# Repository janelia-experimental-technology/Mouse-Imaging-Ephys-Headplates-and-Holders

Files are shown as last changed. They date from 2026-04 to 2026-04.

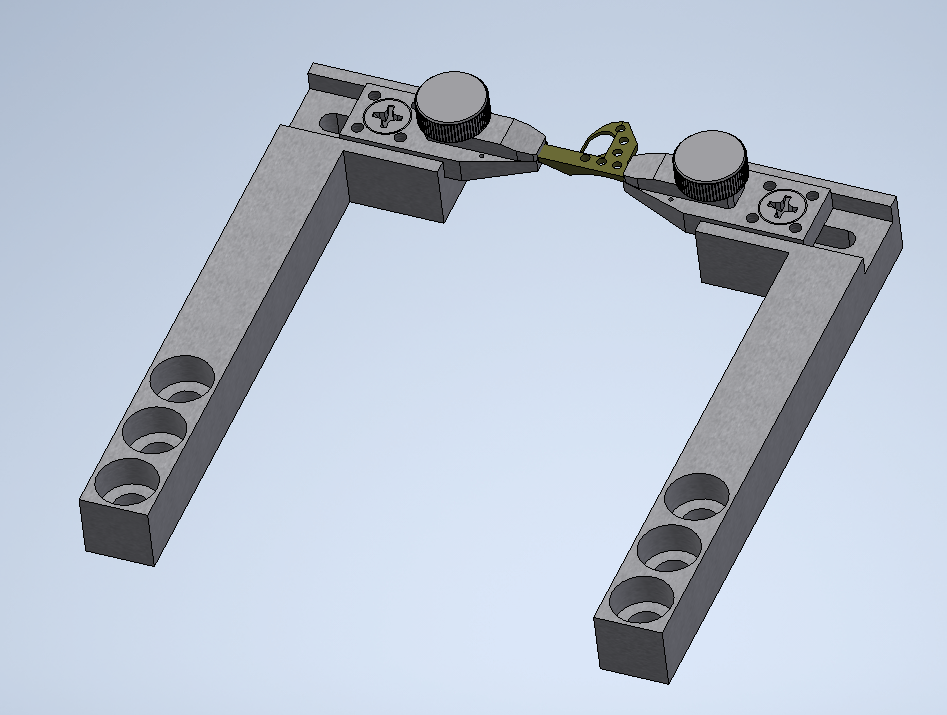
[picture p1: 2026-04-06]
Headbar and Holders.png

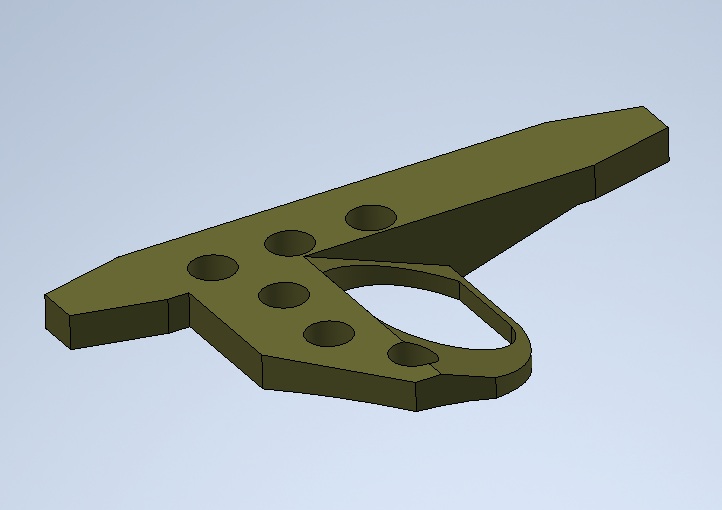
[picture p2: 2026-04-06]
Barrel Sloped Headbar.png

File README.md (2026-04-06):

### Mouse Headplates and Holders for Imaging and Electrophysiology

Researchers at Janelia have designed several head plates for live mouse imaging and electrophysiology experiments in collaboration with jET. 

The head plates are attached to the skull of the mouse typically with dental cement, and are used to locate the brain to the microscope. 

The Barrel Ctx Plate (Sloped Left) Headpost was developed by and used extensively in the Svoboda lab for in vivo imaging of the barrel cortex and other cortical areas (e.g. Huber et al 2012). The Headpost with three epoxy holes was used by the Svoboda lab for electrophysiology experiments. 

Opportunity: Free to make for Non-Profit Research by downloading the design here. See included hardware license.

Rights and designs available for Commercial License. Janelia makes no endorsements or guarantees of licensee products.

For inquiries, please contact innovation@janelia.hhmi.org and reference this repository.

To cite the designs, please use DOI: https://doi.org/10.25378/janelia.31945893

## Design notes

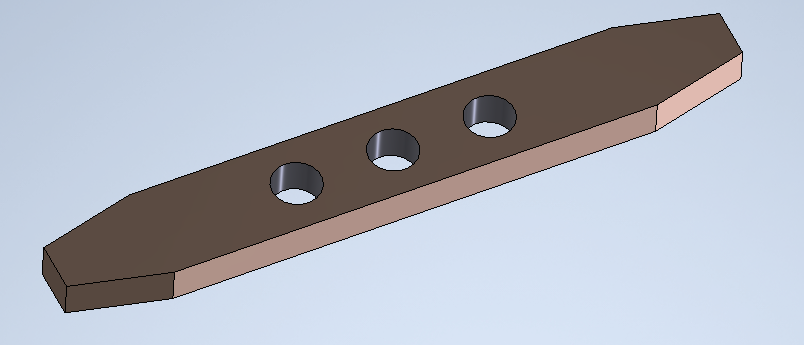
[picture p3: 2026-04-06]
3 Hole Headbar.png

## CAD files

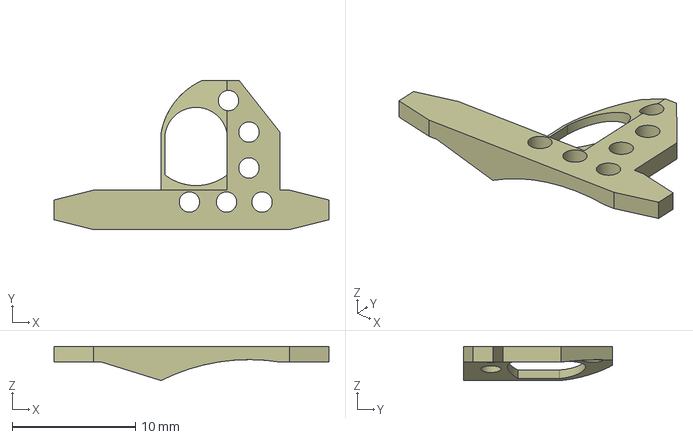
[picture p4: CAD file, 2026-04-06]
Part Files/JF-JM-HC0011 BarrelCtxPlateSlopedLeft Rev A.stp
22.3 x 12.1 x 2.77 mm

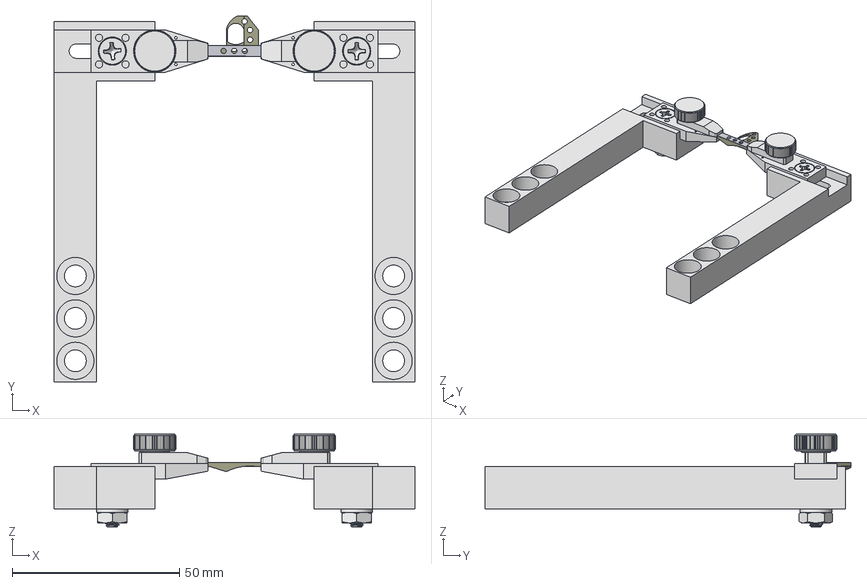
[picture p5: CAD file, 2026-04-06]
Assembly Files/J005779 HEAD POST AND MOUNTING BARS Rev A.stp
107.9 x 109.6 x 27.8 mm
JF-JM-HC0011
J005774 x 2
J005776 x 2
J005772
J005771
91771A197 x 2
92141A009 x 2
91185A440 x 2
91841A009 x 2
J001375

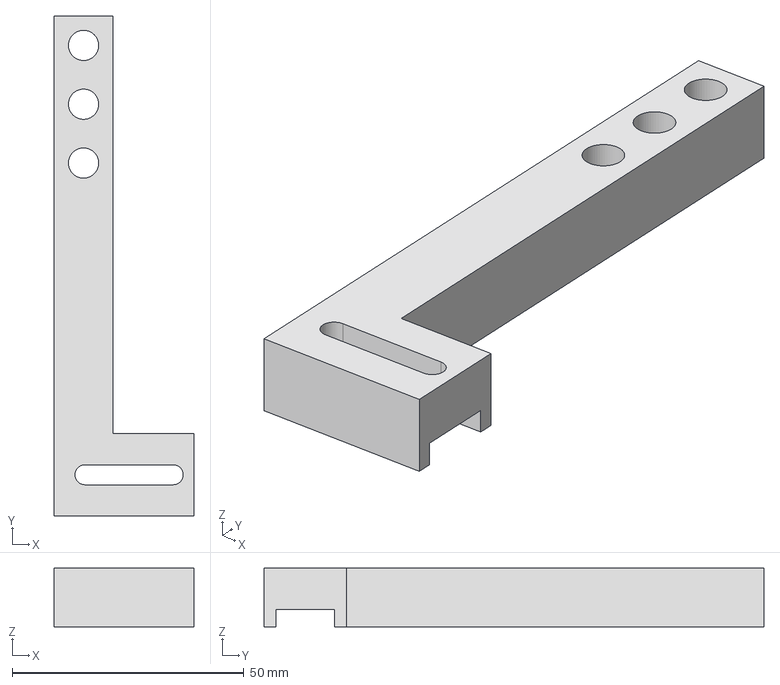
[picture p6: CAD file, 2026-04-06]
Part Files/J005772 HEAD MOUNT ARM ML Rev -.stp
30.1 x 107.9 x 12.7 mm

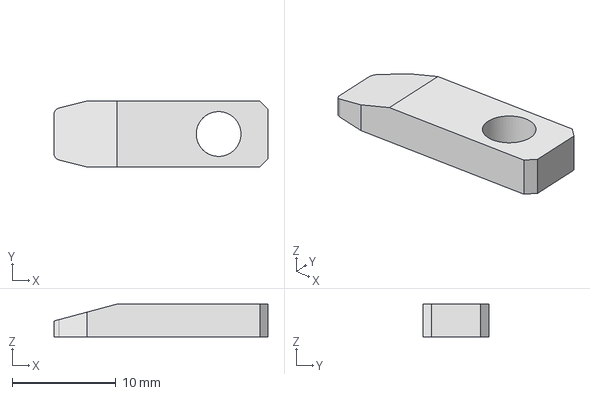
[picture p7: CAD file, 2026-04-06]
Part Files/J005776 HeadPostHolderTop Rev -.stp
20.6 x 6.35 x 3.17 mm

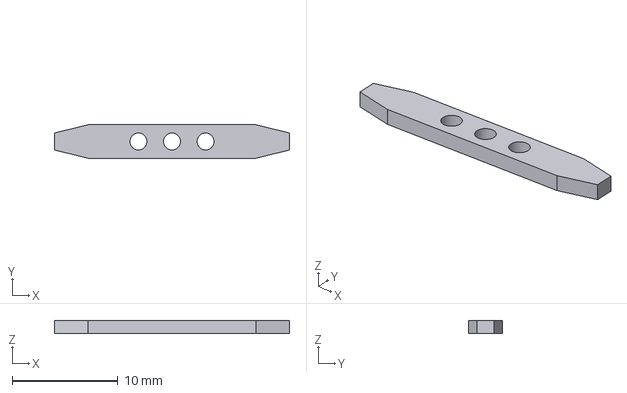
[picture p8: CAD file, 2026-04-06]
Part Files/J001375 KS style headpost with three epoxy holes Rev -.stp
22.2 x 3.18 x 1.27 mm

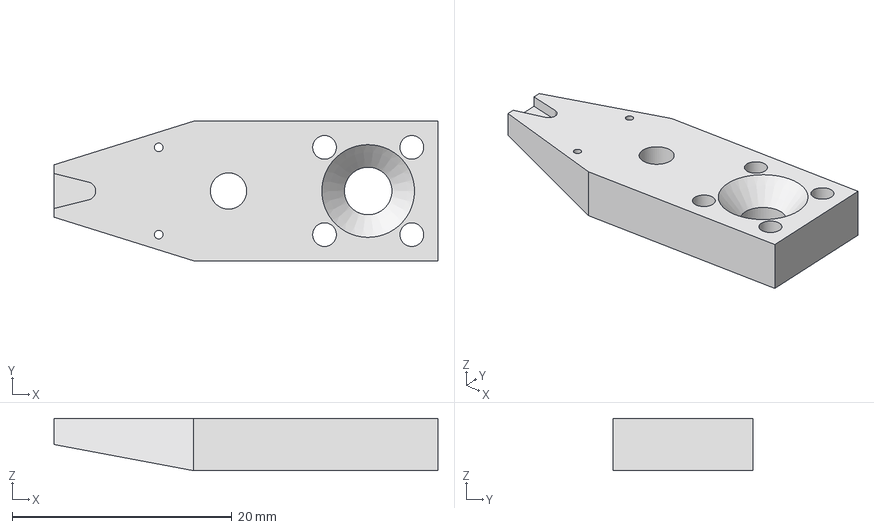
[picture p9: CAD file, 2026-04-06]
Part Files/J005774 HeadPostHolderBottom Rev -.stp
34.9 x 12.7 x 4.76 mm

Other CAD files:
Part Files/J005771 HEAD MOUNT ARM MR Rev -.stp
Inventor Pack And Go/91185A440.ipt
Inventor Pack And Go/91771A197.ipt
Inventor Pack And Go/91841A009.ipt
Inventor Pack And Go/92141A009.ipt
Inventor Pack And Go/BarrelCtxPlateSlopedLeft.ipt
Inventor Pack And Go/HEAD MOUNT ARM ML.ipt
Inventor Pack And Go/HEAD MOUNT ARM MR.ipt
Inventor Pack And Go/HEAD POST AND MOUNTING BARS.iam
Inventor Pack And Go/HeadPostHolderBottom.ipt
Inventor Pack And Go/HeadPostHolderTop.ipt
Inventor Pack And Go/KS style headpost with three epoxy holes.ipt

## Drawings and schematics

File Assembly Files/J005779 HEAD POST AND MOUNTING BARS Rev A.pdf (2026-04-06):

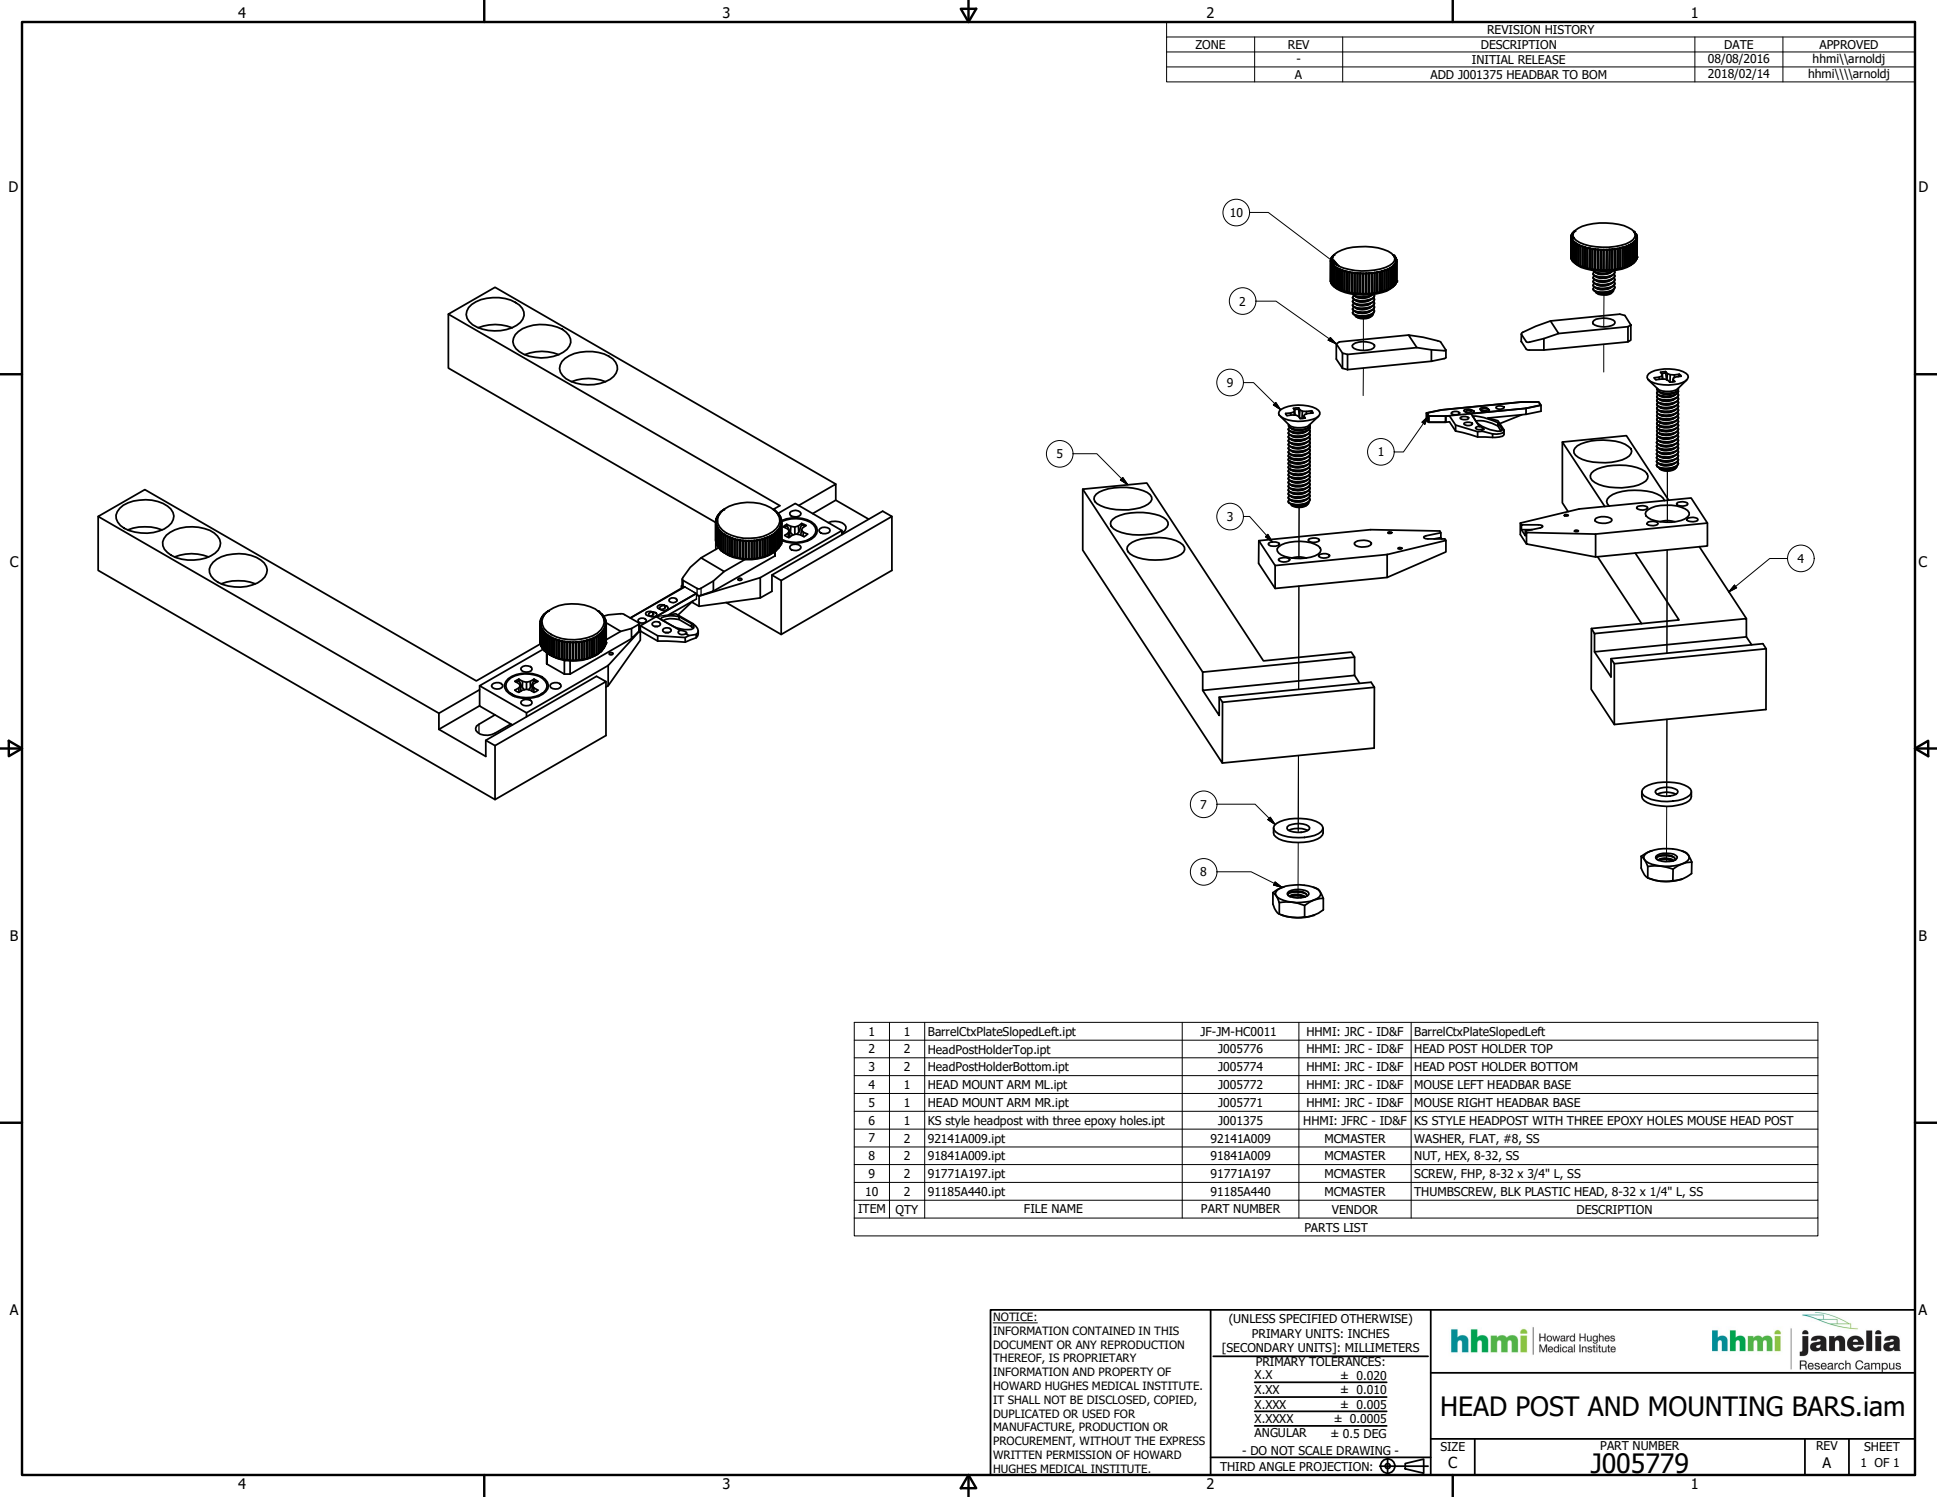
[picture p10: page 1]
PARTS LIST; PART NUMBER; 1 OF 1 THIRD ANGLE PROJECTION:; ± 0.020 ± 0.010 ± 0.005 ± 0.0005 ± 0.5 DEG; REVISION HISTORY

ZONE | REV | DESCRIPTION | DATE | APPROVED

- | INITIAL RELEASE | 08/08/2016 | hhmi\\arnoldj
A | ADD J001375 HEADBAR TO BOM | 2018/02/14 | hhmi\\\\arnoldj

1 | 1 | BarrelCtxPlateSlopedLeft.ipt | JF-JM-HC0011 | HHMI: JRC - ID&F | BarrelCtxPlateSlopedLeft
2 | 2 | HeadPostHolderTop.ipt | J005776 | HHMI: JRC - ID&F | HEAD POST HOLDER TOP
3 | 2 | HeadPostHolderBottom.ipt | J005774 | HHMI: JRC - ID&F | HEAD POST HOLDER BOTTOM
4 | 1 | HEAD MOUNT ARM ML.ipt | J005772 | HHMI: JRC - ID&F | MOUSE LEFT HEADBAR BASE
5 | 1 | HEAD MOUNT ARM MR.ipt | J005771 | HHMI: JRC - ID&F | MOUSE RIGHT HEADBAR BASE
6 | 1 | KS style headpost with three epoxy holes.ipt | J001375 | HHMI: JFRC - ID&F | KS STYLE HEADPOST WITH THREE EPOXY HOLES MOUSE HEAD POST
7 | 2 | 92141A009.ipt | 92141A009 | MCMASTER | WASHER, FLAT, #8, SS
8 | 2 | 91841A009.ipt | 91841A009 | MCMASTER | NUT, HEX, 8-32, SS
9 | 2 | 91771A197.ipt | 91771A197 | MCMASTER | SCREW, FHP, 8-32 x 3/4" L, SS
10 | 2 | 91185A440.ipt | 91185A440 | MCMASTER | THUMBSCREW, BLK PLASTIC HEAD, 8-32 x 1/4" L, SS
ITEM | QTY | FILE NAME | PART NUMBER | VENDOR | DESCRIPTION

NOTICE:
INFORMATION CONTAINED IN THIS
DOCUMENT OR ANY REPRODUCTION
THEREOF, IS PROPRIETARY
INFORMATION AND PROPERTY OF
HOWARD HUGHES MEDICAL INSTITUTE.
IT SHALL NOT BE DISCLOSED, COPIED,
DUPLICATED OR USED FOR
MANUFACTURE, PRODUCTION OR
PROCUREMENT, WITHOUT THE EXPRESS
WRITTEN PERMISSION OF HOWARD
HUGHES MEDICAL INSTITUTE.

(UNLESS SPECIFIED OTHERWISE)
PRIMARY UNITS: INCHES
[SECONDARY UNITS]: MILLIMETERS
PRIMARY TOLERANCES:
X.XXX
X.XXXX
ANGULAR
- DO NOT SCALE DRAWING -

HEAD POST AND MOUNTING BARS.iam

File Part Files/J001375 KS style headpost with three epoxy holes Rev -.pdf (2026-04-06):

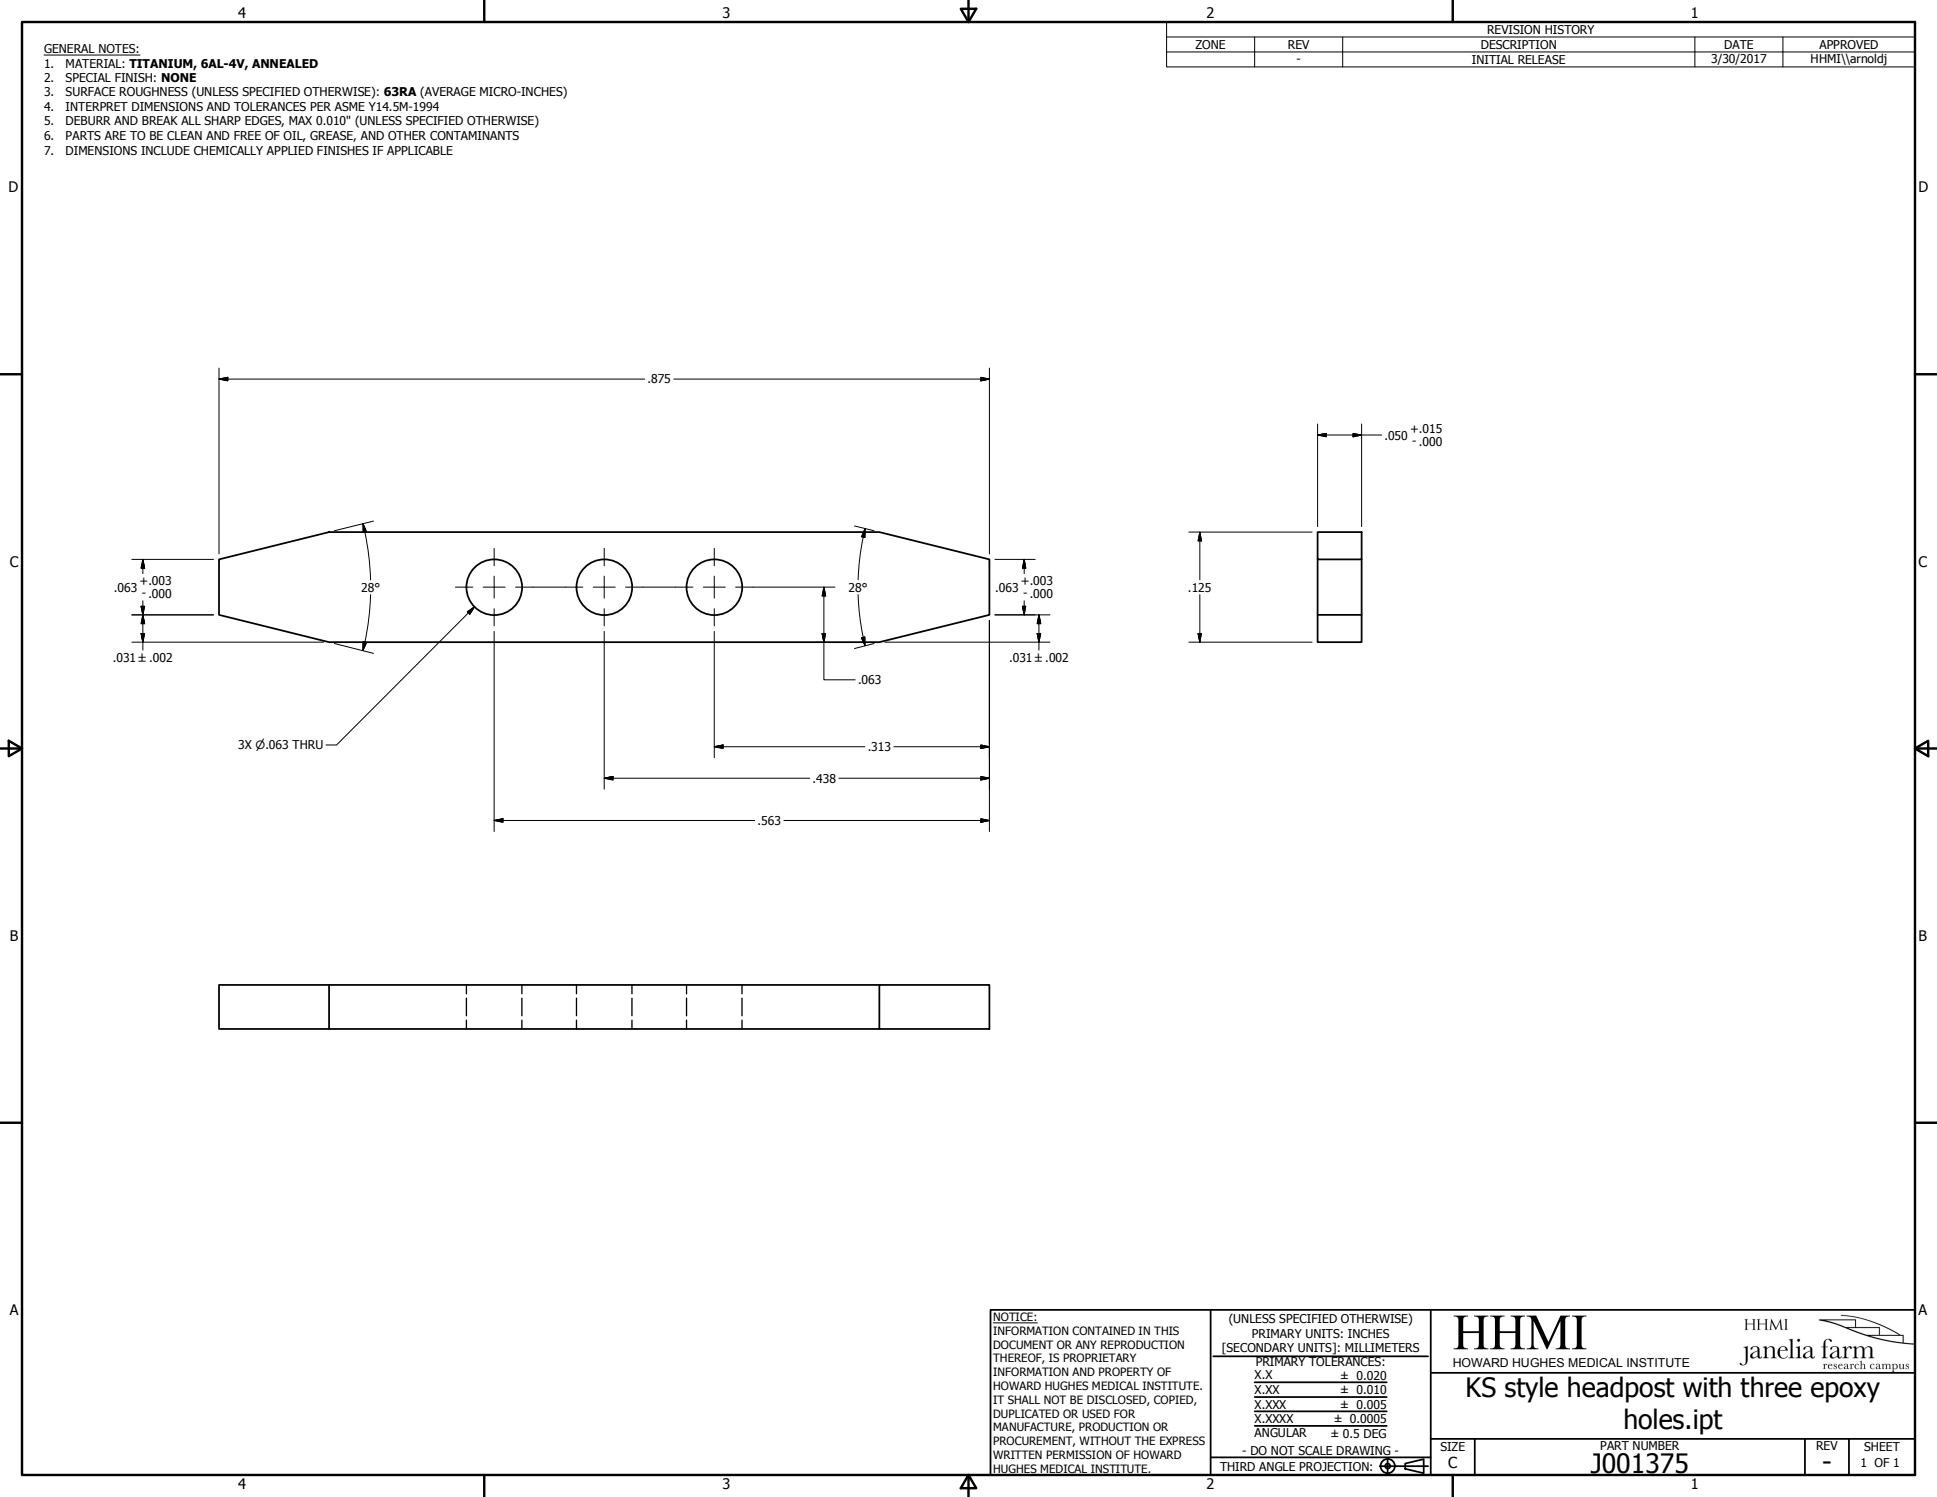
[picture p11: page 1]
PART NUMBER; HHMI; SIZE; REV; SHEET; 1 OF 1 THIRD ANGLE PROJECTION:; ± 0.020 ± 0.010 ± 0.005 ± 0.0005 ± 0.5 DEG; holes.ipt; REVISION HISTORY; ZONE; DESCRIPTION; DATE; APPROVED; INITIAL RELEASE; HHMI\\arnoldj; 3X P.063 THRU

GENERAL NOTES:
1. MATERIAL: TITANIUM, 6AL-4V, ANNEALED
2. SPECIAL FINISH: NONE
3. SURFACE ROUGHNESS (UNLESS SPECIFIED OTHERWISE): 63RA (AVERAGE MICRO-INCHES)
4. INTERPRET DIMENSIONS AND TOLERANCES PER ASME Y14.5M-1994
5. DEBURR AND BREAK ALL SHARP EDGES, MAX 0.010" (UNLESS SPECIFIED OTHERWISE)
6. PARTS ARE TO BE CLEAN AND FREE OF OIL, GREASE, AND OTHER CONTAMINANTS
7. DIMENSIONS INCLUDE CHEMICALLY APPLIED FINISHES IF APPLICABLE

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

HOWARD HUGHES MEDICAL INSTITUTE
KS style headpost with three epoxy

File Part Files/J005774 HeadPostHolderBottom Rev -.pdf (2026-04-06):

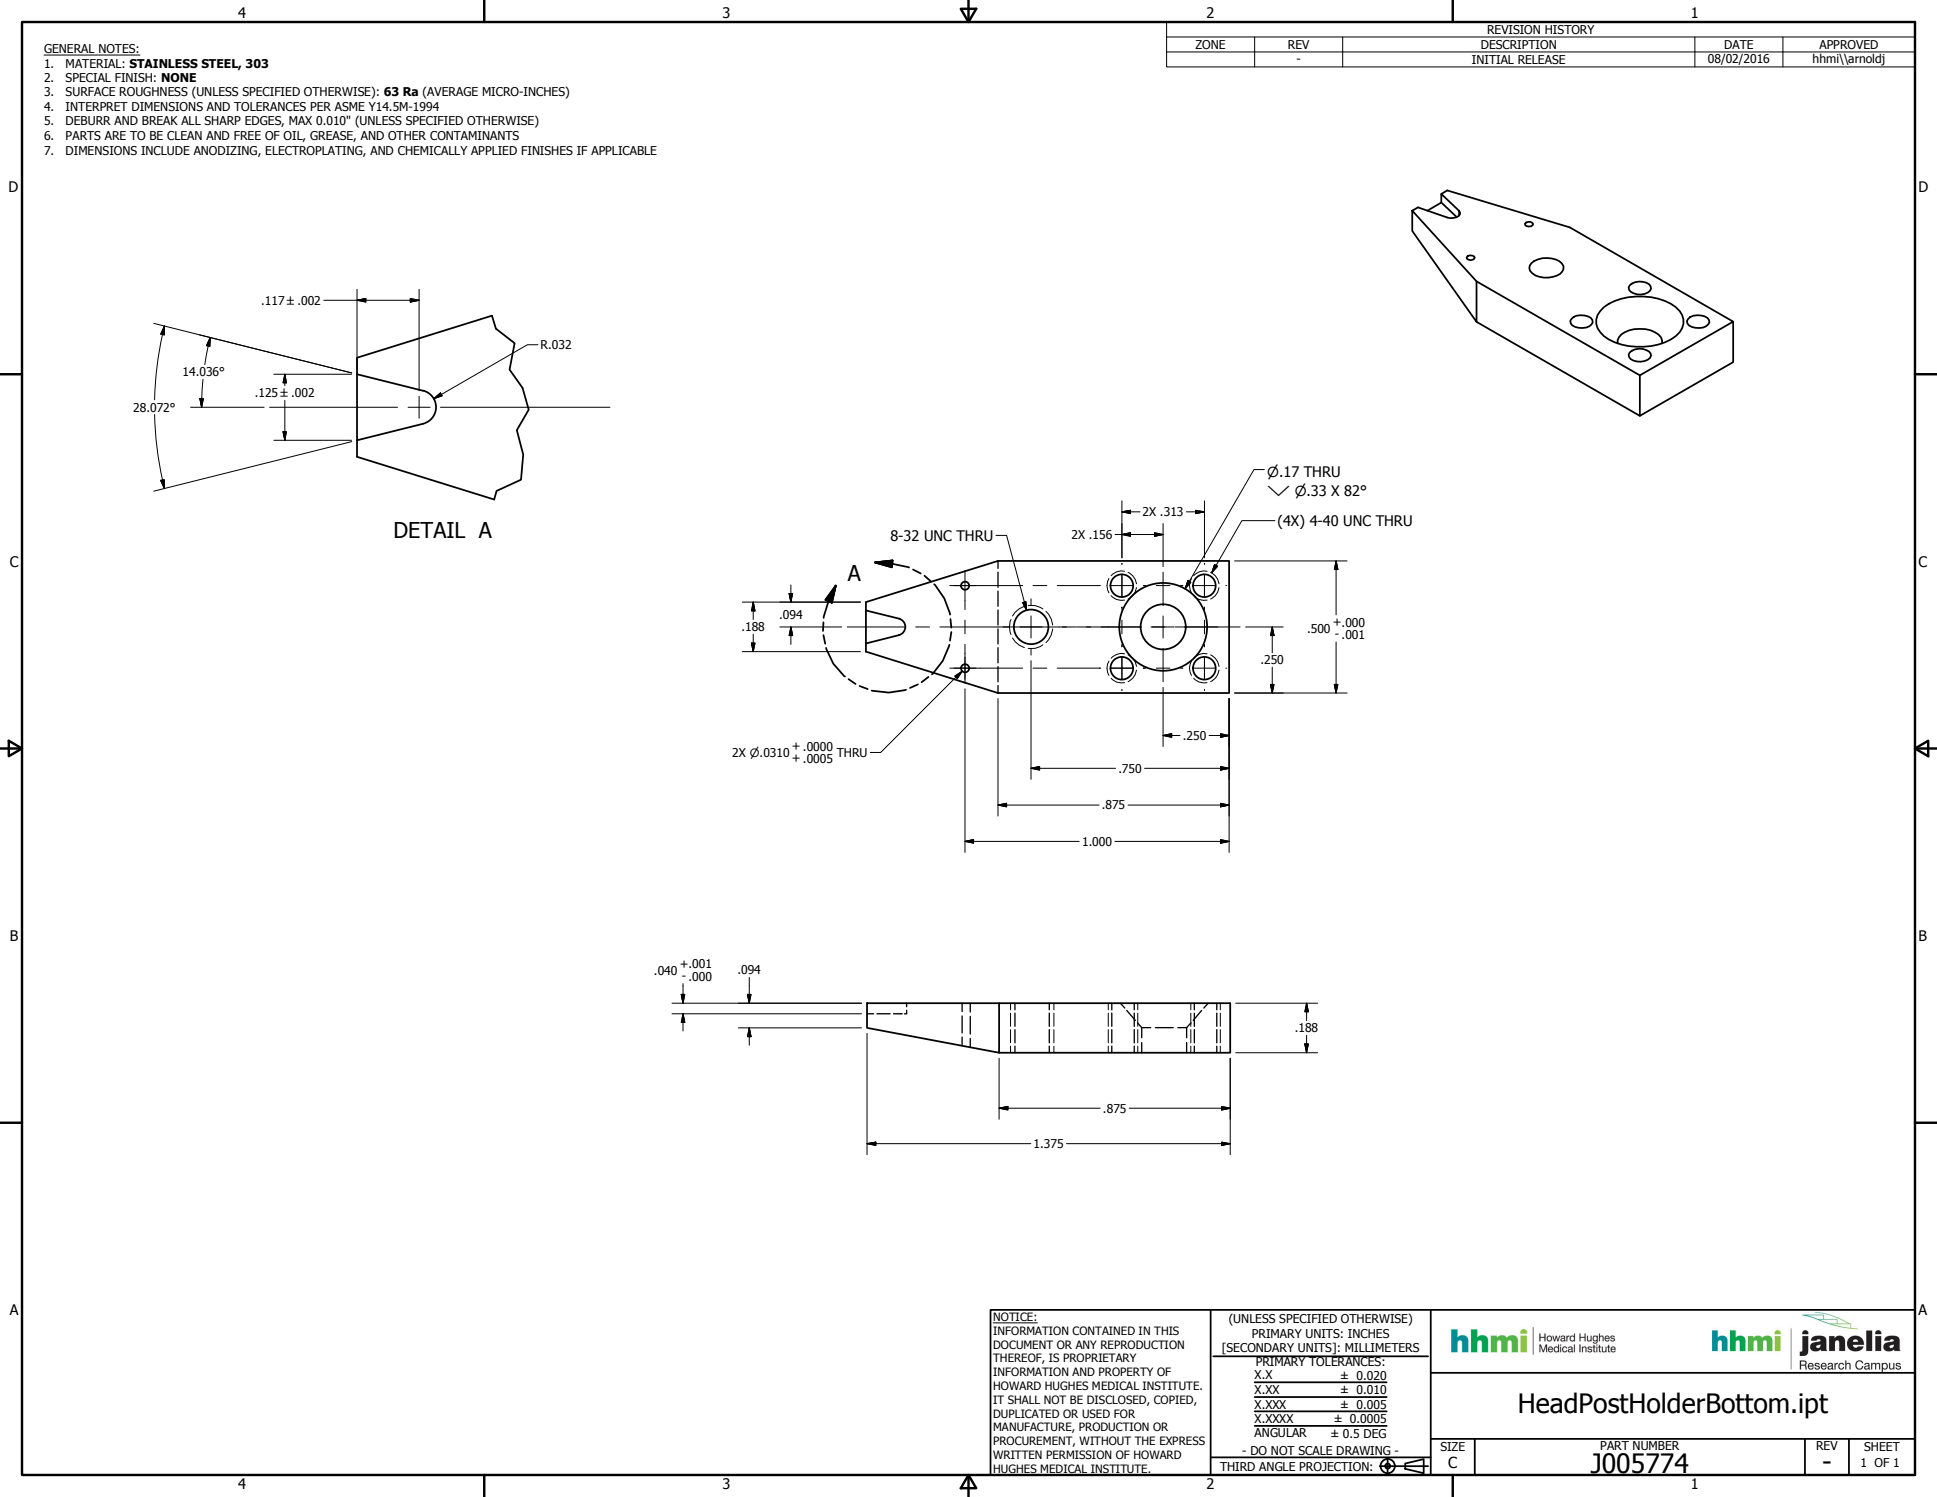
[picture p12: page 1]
DETAIL A; PART NUMBER; SIZE; REV; SHEET; 1 OF 1 THIRD ANGLE PROJECTION:; ± 0.020 ± 0.010 ± 0.005 ± 0.0005 ± 0.5 DEG; HeadPostHolderBottom.ipt; REVISION HISTORY; ZONE; DESCRIPTION; DATE; APPROVED; INITIAL RELEASE; hhmi\\arnoldj; (4X) 4-40 UNC THRU; P.17 THRU Y P.33 X 82°; 8-32 UNC THRU; THRU

GENERAL NOTES:
1. MATERIAL: STAINLESS STEEL, 303
2. SPECIAL FINISH: NONE
3. SURFACE ROUGHNESS (UNLESS SPECIFIED OTHERWISE): 63 Ra (AVERAGE MICRO-INCHES)
4. INTERPRET DIMENSIONS AND TOLERANCES PER ASME Y14.5M-1994
5. DEBURR AND BREAK ALL SHARP EDGES, MAX 0.010" (UNLESS SPECIFIED OTHERWISE)
6. PARTS ARE TO BE CLEAN AND FREE OF OIL, GREASE, AND OTHER CONTAMINANTS
7. DIMENSIONS INCLUDE ANODIZING, ELECTROPLATING, AND CHEMICALLY APPLIED FINISHES IF APPLICABLE

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
